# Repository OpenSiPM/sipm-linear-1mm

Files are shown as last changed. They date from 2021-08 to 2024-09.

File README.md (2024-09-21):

# overview
This repository contains a 16 channel linear array detector designed for hyperspectral fluorescense imaging. Each channel is composed of a single 1x1 mm Hamamatsu S14160 SiPM mounted in a carrier board. These feed into 16 pole zero filters and 16 transimpedance amplifiers adapted from the OpenSiPM single channel design.

# pcb
The PCB is a 4 layer board that can be manufactured inexpensive (few dollars plus shipping) from a number of prototyping services. It could additionally be assembled with at least the passive components on relatively inexpensive, or it can be hand soldered via reflow. Aside from the Hamamatsdu SiPM, the components are stock at Digikey/Mouser.

[Linear array bill of materials](http://htmlpreview.github.io/?https://github.com/OpenSiPM/sipm-linear-1mm/blob/main/sipm-linear-s14160/bom/ibom.html)

# power supply
The linear sipm PCB requires a bipolar power supply capable of powering the 16 OPA847 opamps, which have about 20 mA of quescent current each on top of any output current.  This is supplied by the power-supply-linear-array project, which uses two sets of linear and negative regulators combined with a charge pump to generate the required currents. 

[Power supply bill of materials](http://htmlpreview.github.io/?https://github.com/OpenSiPM/sipm-linear-1mm/blob/main/power-supply-linear-array/kicad/bom/ibom.html)

# bias generator
The bias generator provides the high voltage (~49V) required to bias the SPAD cells in the SiPM. Two versions are provided, a standard one using USB-C and a modified one with a second USB-C connector that allows connecting to an external USB-C power supply.  This can be useful as the total array power is about 3W, and so exceeds the 2.5W supplied by USB2 devices.  By using the second port, the power per port can be kept under 500 mA for hubs and hosts that are not USB3 or USB-C.  

[Power supply bill of materials](http://htmlpreview.github.io/?https://github.com/OpenSiPM/sipm-linear-1mm/blob/main/bias-control-lt8364-linear/bom/ibom.html)

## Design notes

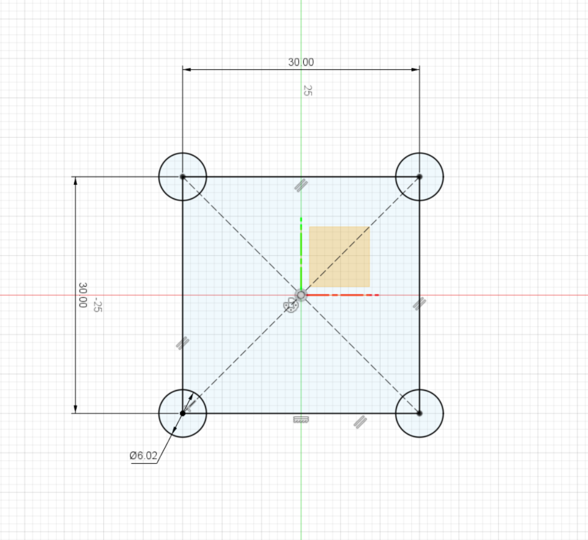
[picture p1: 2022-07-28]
mechanical diagram.png

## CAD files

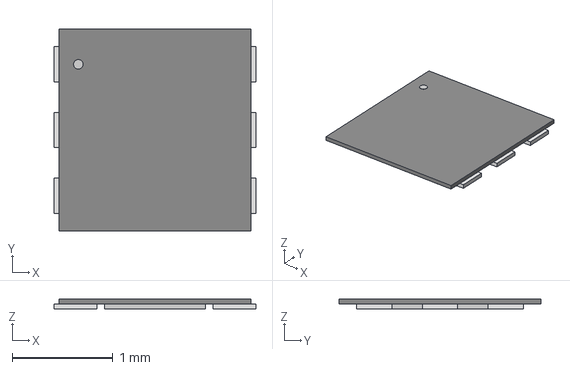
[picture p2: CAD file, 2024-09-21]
bias-control-lt8364-linear-two-usb/step/CP_6_3.step
2.00 x 2.00 x 0.103 mm

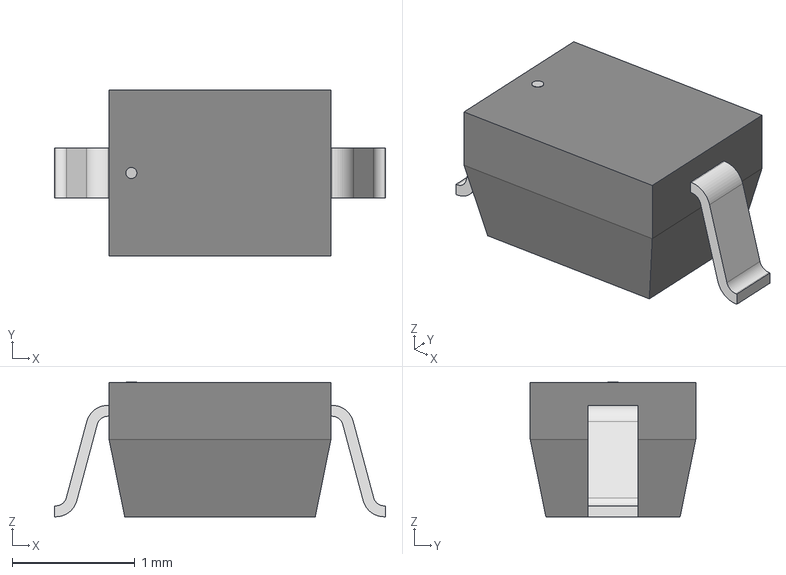
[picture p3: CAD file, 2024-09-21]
bias-control-lt8364-linear/step/SOD323F_NXP.step
2.69 x 1.35 x 1.09 mm

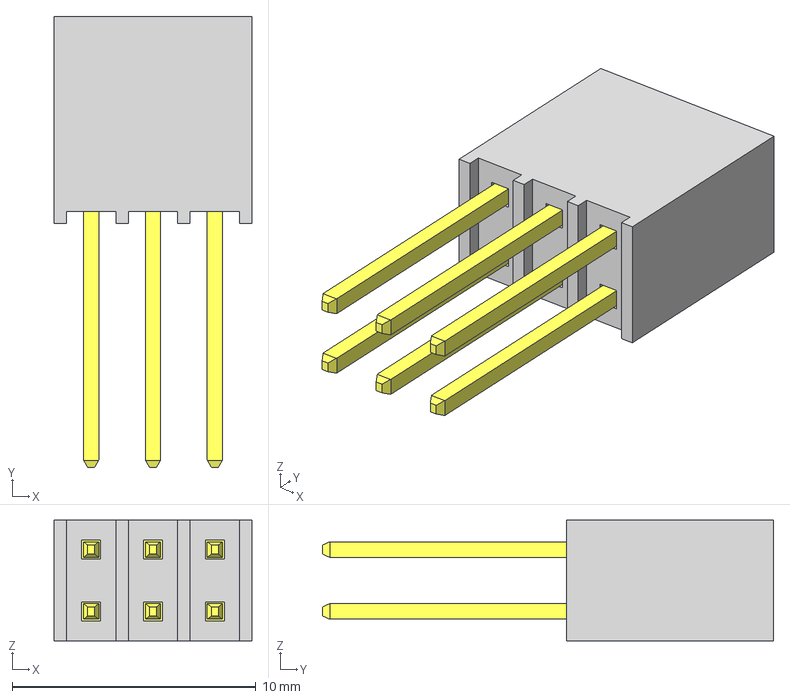
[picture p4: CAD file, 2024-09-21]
power-supply-linear-array/kicad/step/SSQ-103-03-G-D.step
8.13 x 18.5 x 4.95 mm
_T1SSQ-103-03-G-D
_P2SSQ-103-03-G-D

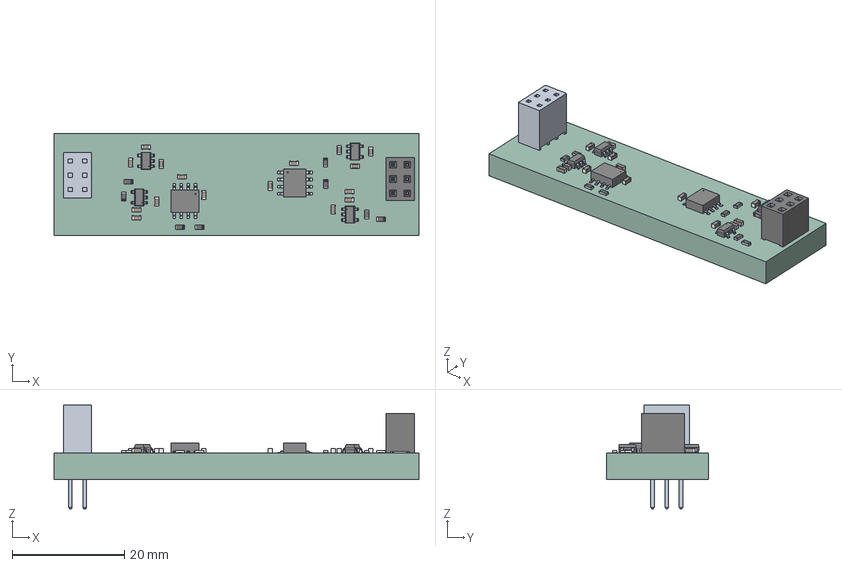
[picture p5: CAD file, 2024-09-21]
power-supply-linear-array/manufacturing/psu.step
65.0 x 18.1 x 18.5 mm
psu PCB

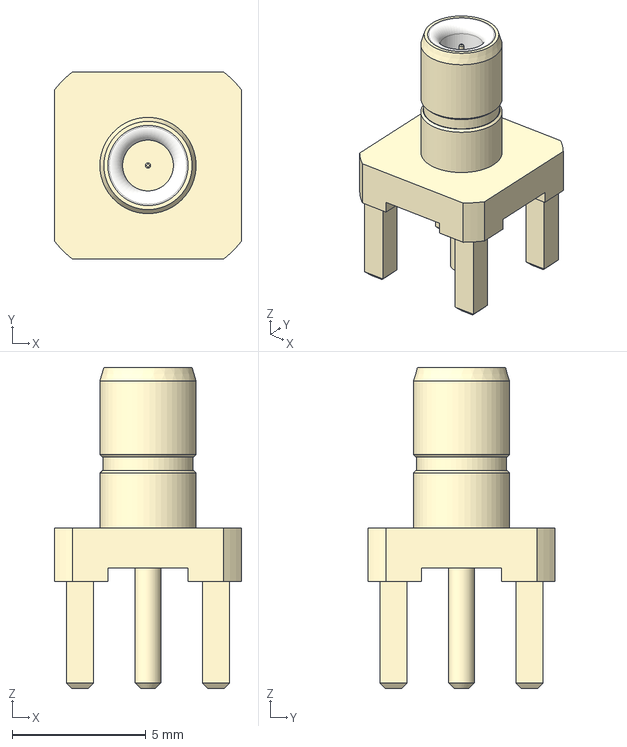
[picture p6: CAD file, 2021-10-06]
sipm-linear-s14160/step/SMB standing.step
7.00 x 7.00 x 12.0 mm

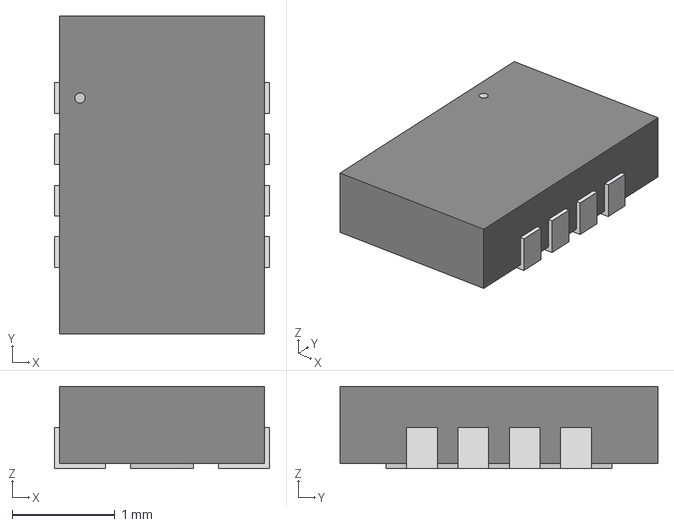
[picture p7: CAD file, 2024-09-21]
bias-control-lt8364-linear-two-usb/step/DFN-8_DDB_LIT-M.step
2.10 x 3.10 x 0.803 mm

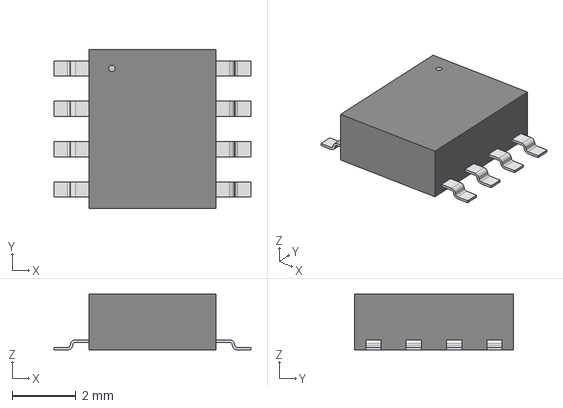
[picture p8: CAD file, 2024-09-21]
power-supply-linear-array/kicad/step/21-0041B_8_MXM.step
6.20 x 5.00 x 1.75 mm

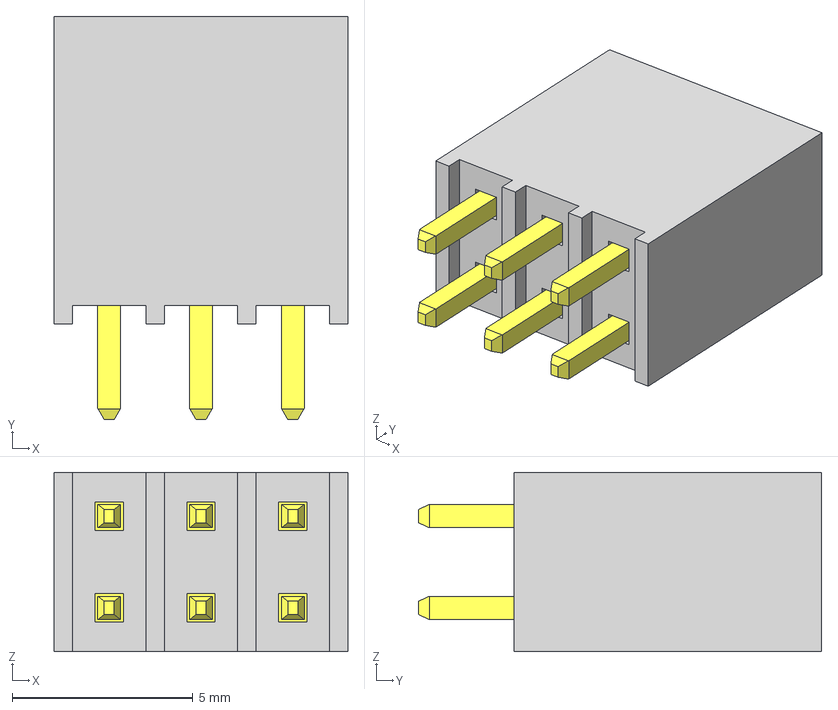
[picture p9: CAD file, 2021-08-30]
sipm-linear-s14160/step/SSQ-103-01-G-D.step
8.13 x 11.2 x 4.95 mm
_T1SSQ-103-01-G-D
_P2SSQ-103-01-G-D

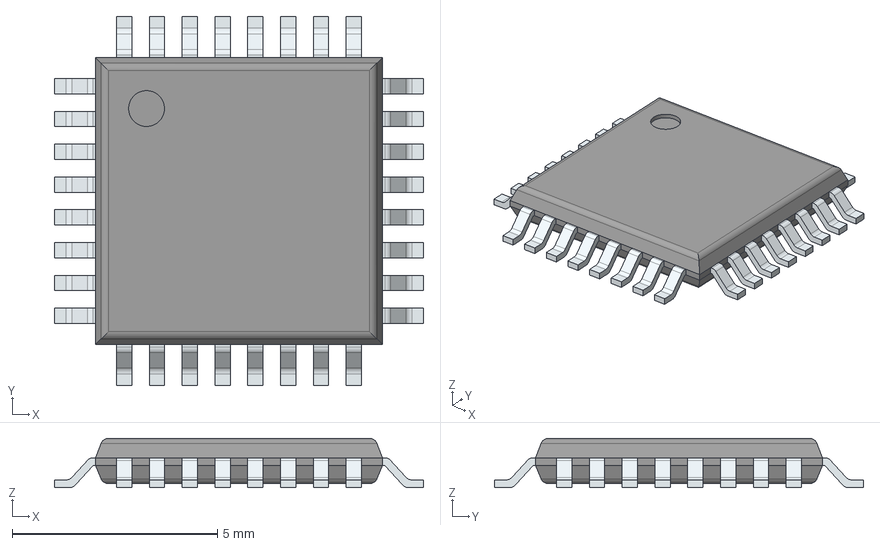
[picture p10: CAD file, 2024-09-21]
bias-control-lt8364-linear-two-usb/step/ATSAMD21E18A-AFT.stp
9.00 x 9.00 x 1.20 mm
PinsArrayLR
PinsArrayTB

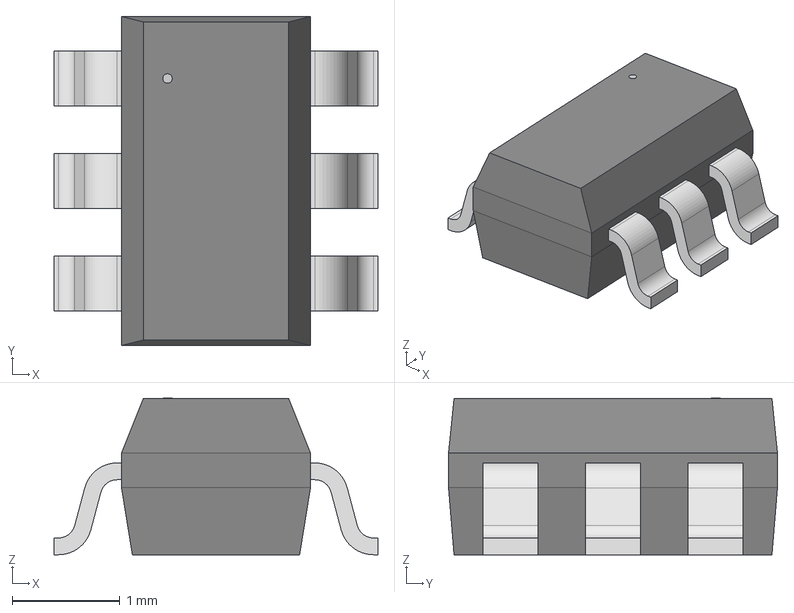
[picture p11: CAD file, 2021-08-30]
power-supply-linear-array/kicad/step/DBV6.step
3.00 x 3.05 x 1.45 mm

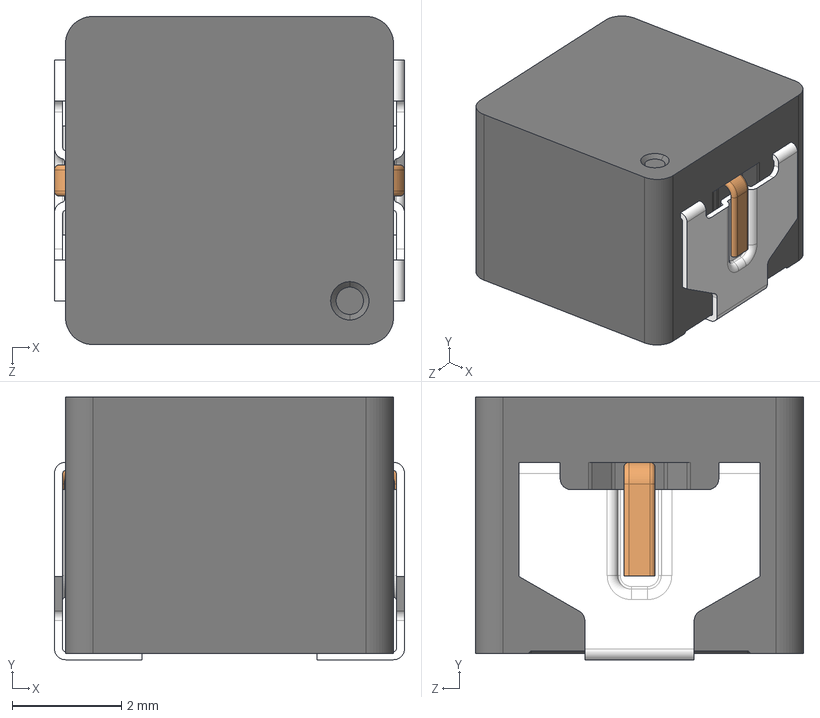
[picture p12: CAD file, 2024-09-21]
bias-control-lt8364-linear/step/ETQP4M3R3KFN.step
6.40 x 4.80 x 6.00 mm

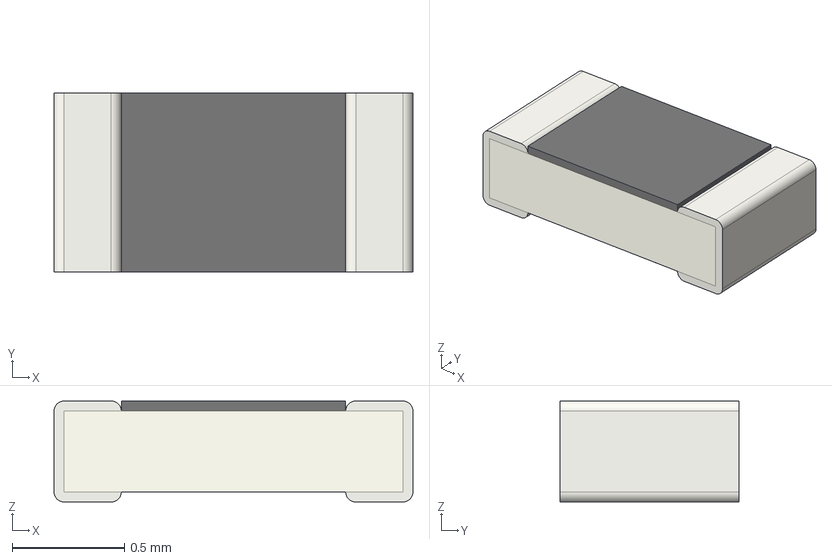
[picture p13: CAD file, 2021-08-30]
power-supply-linear-array/kicad/step/R_0603_1608Metric.step
1.60 x 0.8 x 0.45 mm

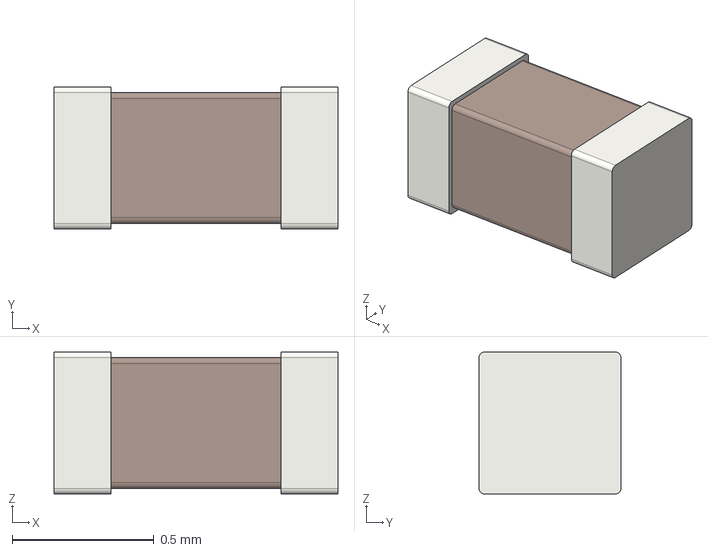
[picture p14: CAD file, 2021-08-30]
sipm-linear-s14160/step/C_0402_1005Metric.step
1.00 x 0.5 x 0.5 mm

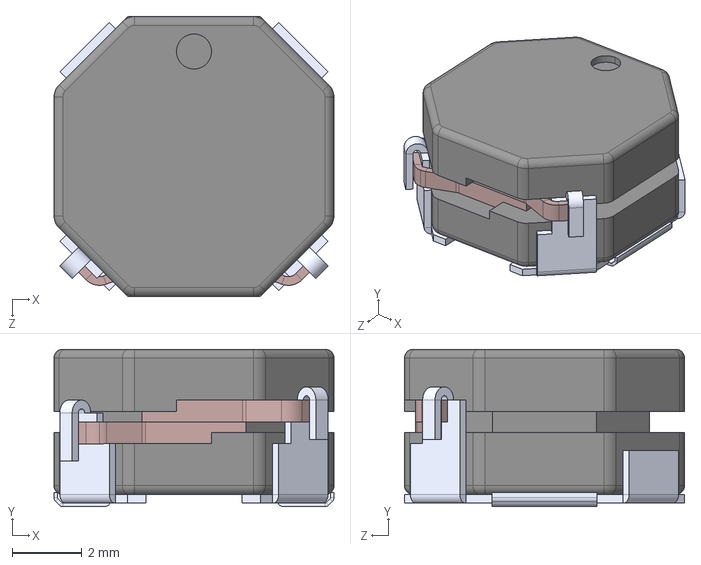
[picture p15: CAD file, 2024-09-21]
bias-control-lt8364-linear-two-usb/step/1217AS-H-3R3N_P3.step
8.00 x 4.50 x 8.00 mm

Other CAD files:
bias-control-lt8364-linear/step/CP_6_3-M.step
bias-control-lt8364-linear-two-usb/step/CP_6_3-L.step
bias-control-lt8364-linear/step/LT3571EUD#PBF.stp
bias-control-lt8364-linear-two-usb/step/878980466.stp
bias-control-lt8364-linear-two-usb/step/CP_6_3-M.step
bias-control-lt8364-linear-two-usb/step/CX80B1-24P_3D_STEP.STEP
bias-control-lt8364-linear-two-usb/step/C_0603_1608Metric.step
bias-control-lt8364-linear-two-usb/step/DFN-8_DDB_LIT-L.step
bias-control-lt8364-linear-two-usb/step/DFN-8_DDB_LIT.step
bias-control-lt8364-linear-two-usb/step/DFN6_2x2MC.step
bias-control-lt8364-linear-two-usb/step/DX07S024WJ3R400--3DModel-STEP-56544.STEP
bias-control-lt8364-linear-two-usb/step/HTSW-103-23-L-D.stp
bias-control-lt8364-linear-two-usb/step/IND_TAIYO_NR6028_TAY.step
bias-control-lt8364-linear-two-usb/step/LT3571EUD#PBF.stp
bias-control-lt8364-linear-two-usb/step/LT8364EMSE#TRPBF.stp
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

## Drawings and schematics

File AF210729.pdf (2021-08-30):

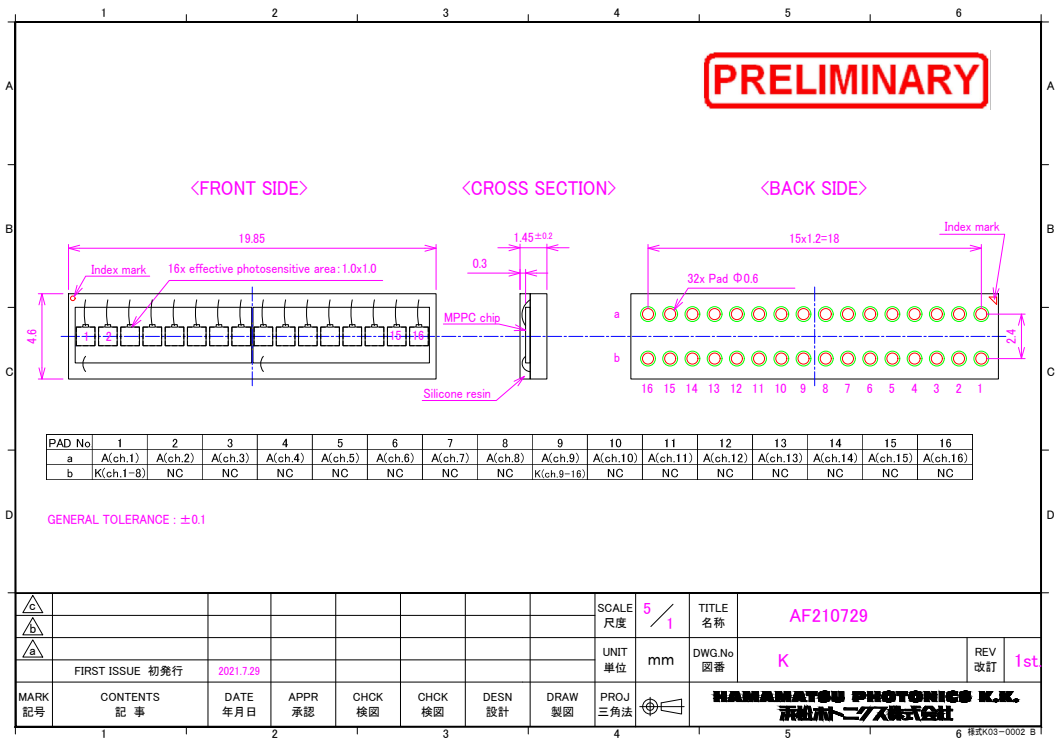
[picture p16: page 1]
15 16 16x effective photosensitive area：1.0x1.0 19.85

2.4 A 6 B 4 5 D 6 様式Ｋ０３－０００２　Ｂ K5 ｍｍ 4 AF210729 C 1 2 3 AB 3 2021.7.29 2 c D ba FIRST ISSUE 初発行 1 C 5 1 MARK 記号 CONTENTS 記 事 DATE 年月日 APPR 承認 CHCK 検図 CHCK 検図 DESN 設計 DRAW 製図 尺度UNIT PROJ 三角法 単位 SCALE 名称 DWG.No 図番 TITLE REV 改訂 1st.

4.6 Index mark 1.45±0.2 0.3 MPPC chip Silicone resin Index mark 32x Pad Φ0.6 <FRONT SIDE> <CROSS SECTION> <BACK SIDE> GENERAL TOLERANCE : ±0.1 16 15 14 13 12 11 10 9 8 7 6 5 4 3 2 1 ba 15x1.2=18

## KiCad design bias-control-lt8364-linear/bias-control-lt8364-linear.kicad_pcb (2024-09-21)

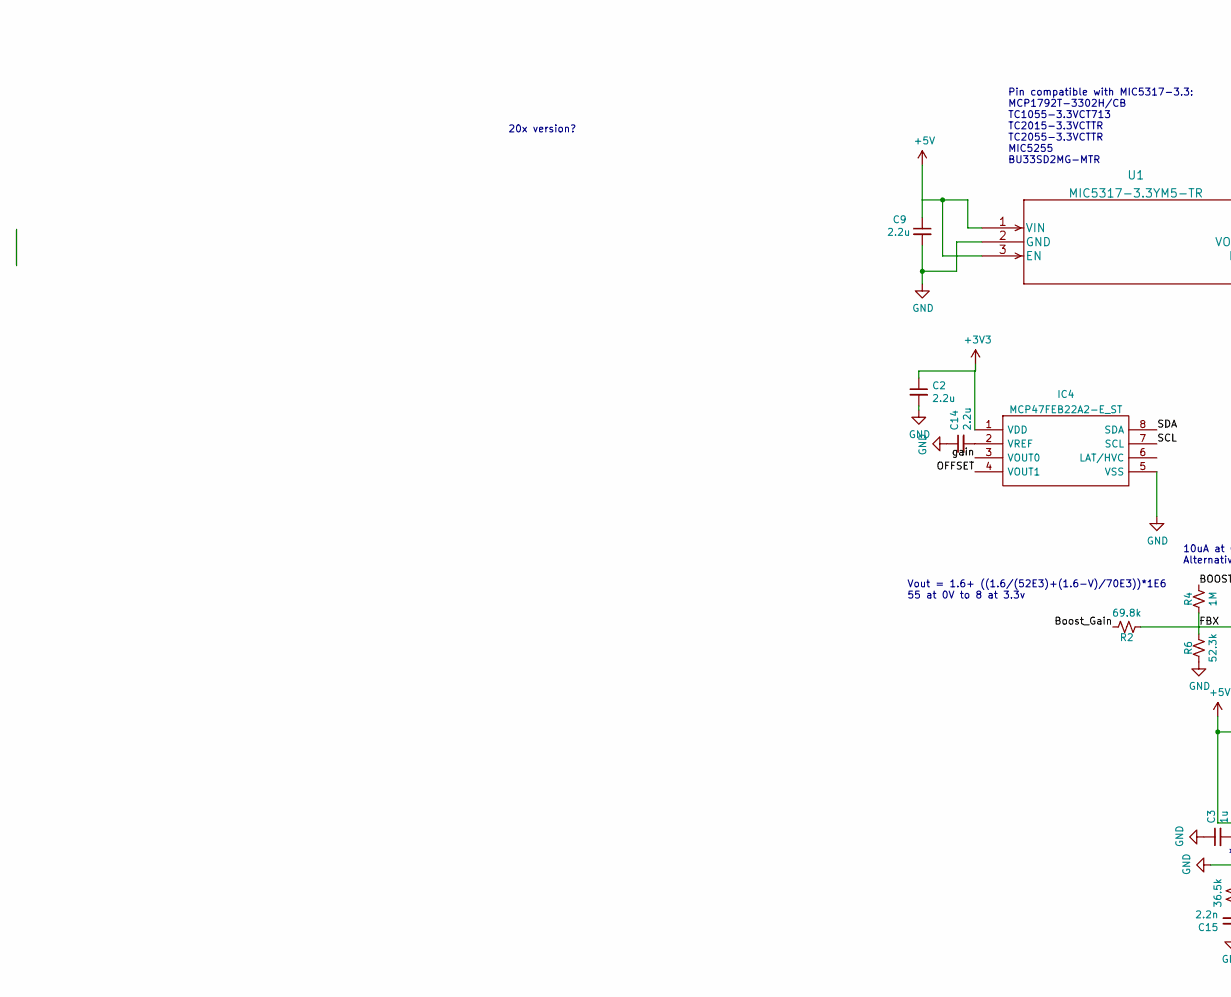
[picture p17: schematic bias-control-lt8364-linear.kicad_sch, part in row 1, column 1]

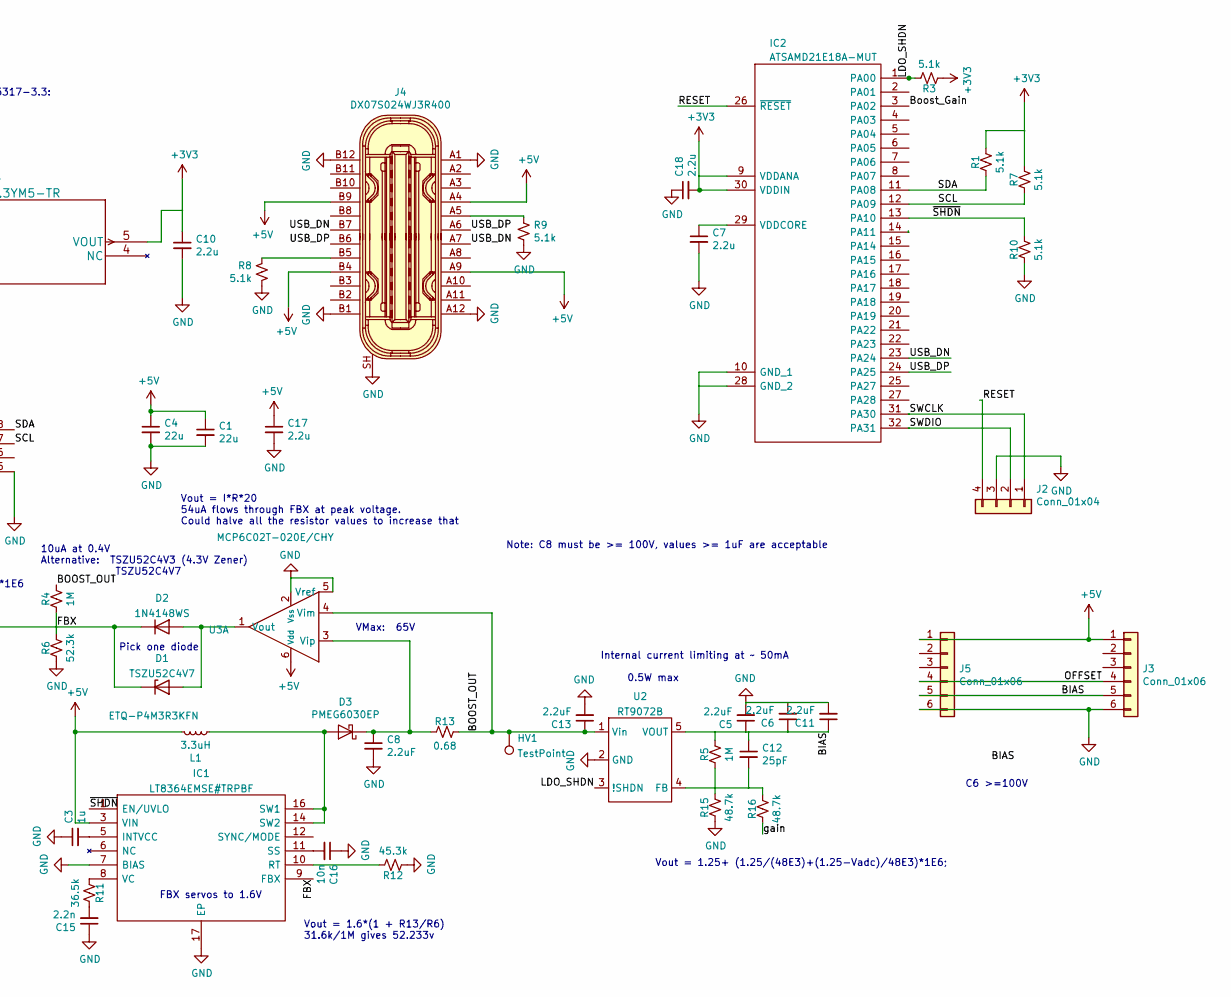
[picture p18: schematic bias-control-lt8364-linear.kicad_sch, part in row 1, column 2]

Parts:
C1, C4: 22u; C_0603_1608Metric; Voltage 10V
C2, C7, C9, C10, C14, C17, C18: 2.2u; C_0402_1005Metric
C3: 1u; C_0402_1005Metric
C5, C6, C8, C11, C13: 2.2uF; C_1206_3216Metric; Voltage 100V
C12: 25pF; C_0402_1005Metric
C15: 2.2n; C_0402_1005Metric
C16: 10n; C_0402_1005Metric
D1: TSZU52C4V7; D_0603_1608Metric
D2: 1N4148WS; D_SOD-323F
D3: PMEG6030EP; D_SOD-128
HV1: TestPoint; TestPoint_Pad_D1.0mm
IC1: LT8364EMSE#TRPBF; LT8364IMSE-PBF; Mouser Part Number 584-LT8364EMSETRPBF
IC2: ATSAMD21E18A-MUT; QFN-32-1EP_5x5mm_Pitch0.5mm; Manufacturer_Part_Number ATSAMD21E18A-AFT
IC4: MCP47FEB22A2-E_ST; SOP65P640X120-8N; Mouser Part Number 579-MCP47FEB22A2EST
J2: Conn_01x04; PinHeader_1x04_P2.54mm_Vertical_SMD_Pin1Right
J3, J5: Conn_01x06; PinHeader_2x03_P2.54mm_Vertical
J4: DX07S024WJ3R400; USB-C_Female_Vert_DX07S024WJ3R400; MPN DX07S024WJ3R400; Digi-Key_PN 670-2950-1-ND
L1: 3.3uH; IND_ETQP4M3R3KFN; MPN ETQ-P4M3R3KFN
R1, R3, R7, R8, R9, R10: 5.1k; R_0402_1005Metric
R2: 69.8k; R_0402_1005Metric
R4, R5: 1M; R_0402_1005Metric
R6: 52.3k; R_0402_1005Metric
R11: 36.5k; R_0402_1005Metric
R12: 45.3k; R_0402_1005Metric
R13: 0.68; R_0402_1005Metric
R15, R16: 48.7k; R_0402_1005Metric
U1: MIC5317-3.3YM5-TR
U2: RT9072B; SOT-23-5
U3: MCP6C02T-020E/CHY; SOT-23-6

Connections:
+3V3: C2.1, C10.1, C18.2, IC2.9 (VDDANA), IC2.30 (VDDIN), IC4.1 (VDD), R1.1, R3.2, R7.1, U1.5 (VOUT)
+5V: C1.1, C4.1, C9.1, C17.1, IC1.3 (VIN), J3.1, J4.A4, J4.A9, J4.B4, J4.B9, J5.1, L1.2, U1.1 (VIN), U1.3 (EN), U3.6 (Vdd)
/BIAS: C5.1, C6.1, C11.1, C12.1, J3.5, J5.5, R5.1, U2.5 (VOUT)
/BOOST_OUT: C13.1, HV1.1, R4.1, R13.1, U2.1 (Vin), U3.4 (Vim)
/Boost_Gain: IC2.3 (PA02), R2.1
/FBX: D1.1 (K), D2.1 (K), IC1.9 (FBX), R2.2, R4.2, R6.1
/LDO_SHDN: IC2.1 (PA00), R3.1, U2.3 (!SHDN)
/OFFSET: IC4.4 (VOUT1), J3.4, J5.4
/RESET: IC2.26 (~RESET), J2.4
/SCL: IC2.12 (PA09), IC4.7 (SCL), R7.2
/SDA: IC2.11 (PA08), IC4.8 (SDA), R1.2
/SWCLK: IC2.31 (PA30), J2.1
/SWDIO: IC2.32 (PA31), J2.2
/USB_DN: IC2.23 (PA24), J4.A7, J4.B7
/USB_DP: IC2.24 (PA25), J4.A6, J4.B6
/gain: IC4.3 (VOUT0), R16.2
/~SHDN: IC1.1 (EN/UVLO), IC2.13 (PA10), R10.1
GND: C1.2, C2.2, C3.1, C4.2, C5.2, C6.2, C7.2, C8.2, C9.2, C10.2, C11.2, C13.2, C14.1, C15.1, C16.1, C17.2, C18.1, IC1.7 (BIAS), IC1.17 (EP), IC2.10 (GND_1), IC2.28 (GND_2), IC2.33 (EP), IC4.5 (VSS), J2.3, J3.6, J4.A1, J4.A12, J4.B1, J4.B12, J4.SH, J5.6, R6.2, R8.2, R9.2, R10.2, R12.2, R15.2, U1.2 (GND), U2.2 (GND), U3.2 (Vss), U3.5 (Vref)
unnamed: C15.2, R11.1
unnamed: D1.2 (A), D2.2 (A), U3.1 (Vout)
unnamed: D3.2 (A), IC1.14 (SW2), IC1.16 (SW1), L1.1
unnamed: C8.1, D3.1 (K), R13.2, U3.3 (Vip)
unnamed: C3.2, IC1.5 (INTVCC)
unnamed: IC1.10 (RT), R12.1
unnamed: C16.2, IC1.11 (SS)
unnamed: IC1.8 (VC), R11.2
unnamed: C7.1, IC2.29 (VDDCORE)
unnamed: C14.2, IC4.2 (VREF)
unnamed: J4.A5, R9.1
unnamed: J4.B5, R8.1
unnamed: C12.2, R5.2, R15.1, R16.1, U2.4 (FB)

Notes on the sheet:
Vout = 1.6*(1 + R13/R6) 31.6k/1M gives 52.233v
Note: C8 must be >= 100V, values >= 1uF are acceptable
Vout = I*R*20 54uA flows through FBX at peak voltage. Could halve all the resistor values to increase that
Pick one diode
Internal current limiting at ~ 50mA
Pin compatible with MIC5317-3.3: MCP1792T-3302H/CB TC1055-3.3VCT713 TC2015-3.3VCTTR TC2055-3.3VCTTR MIC5255 BU33SD2MG-MTR
20x version?
0.5W max
10uA at 0.4V Alternative: TSZU52C4V3 (4.3V Zener) TSZU52C4V7
C6 >=100V
Vout = 1.25+ (1.25/(48E3)+(1.25-Vadc)/48E3)*1E6;
VMax: 65V
Vout = 1.6+ ((1.6/(52E3)+(1.6-V)/70E3))*1E6 55 at 0V to 8 at 3.3v
FBX servos to 1.6V

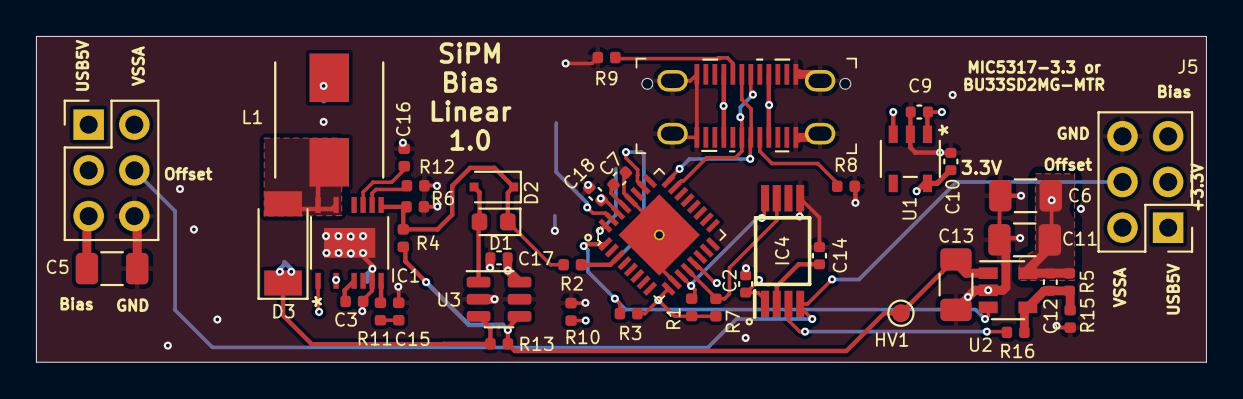
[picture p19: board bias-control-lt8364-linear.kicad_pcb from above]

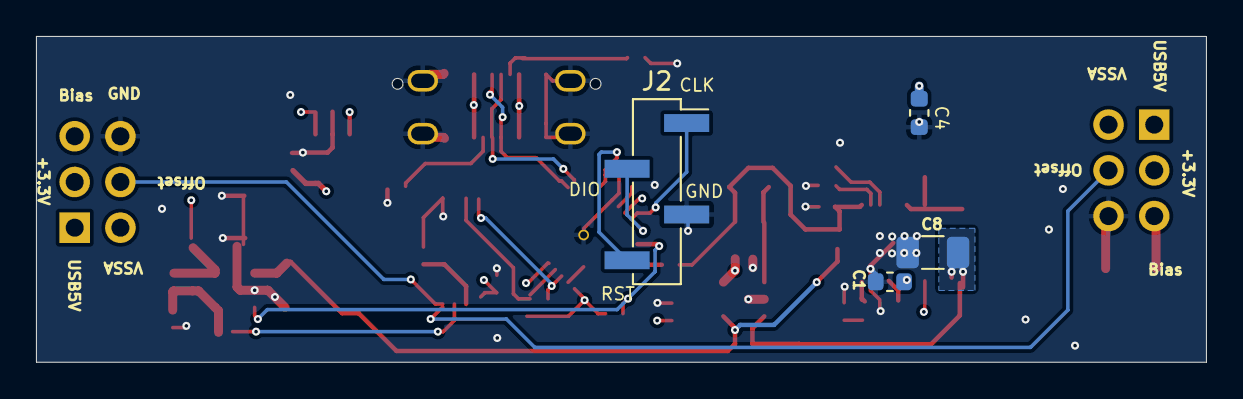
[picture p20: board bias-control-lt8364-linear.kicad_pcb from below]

Board: 4 copper layers, 65.0 x 18.1 mm, 48 parts (4 on the bottom side), 31 nets.

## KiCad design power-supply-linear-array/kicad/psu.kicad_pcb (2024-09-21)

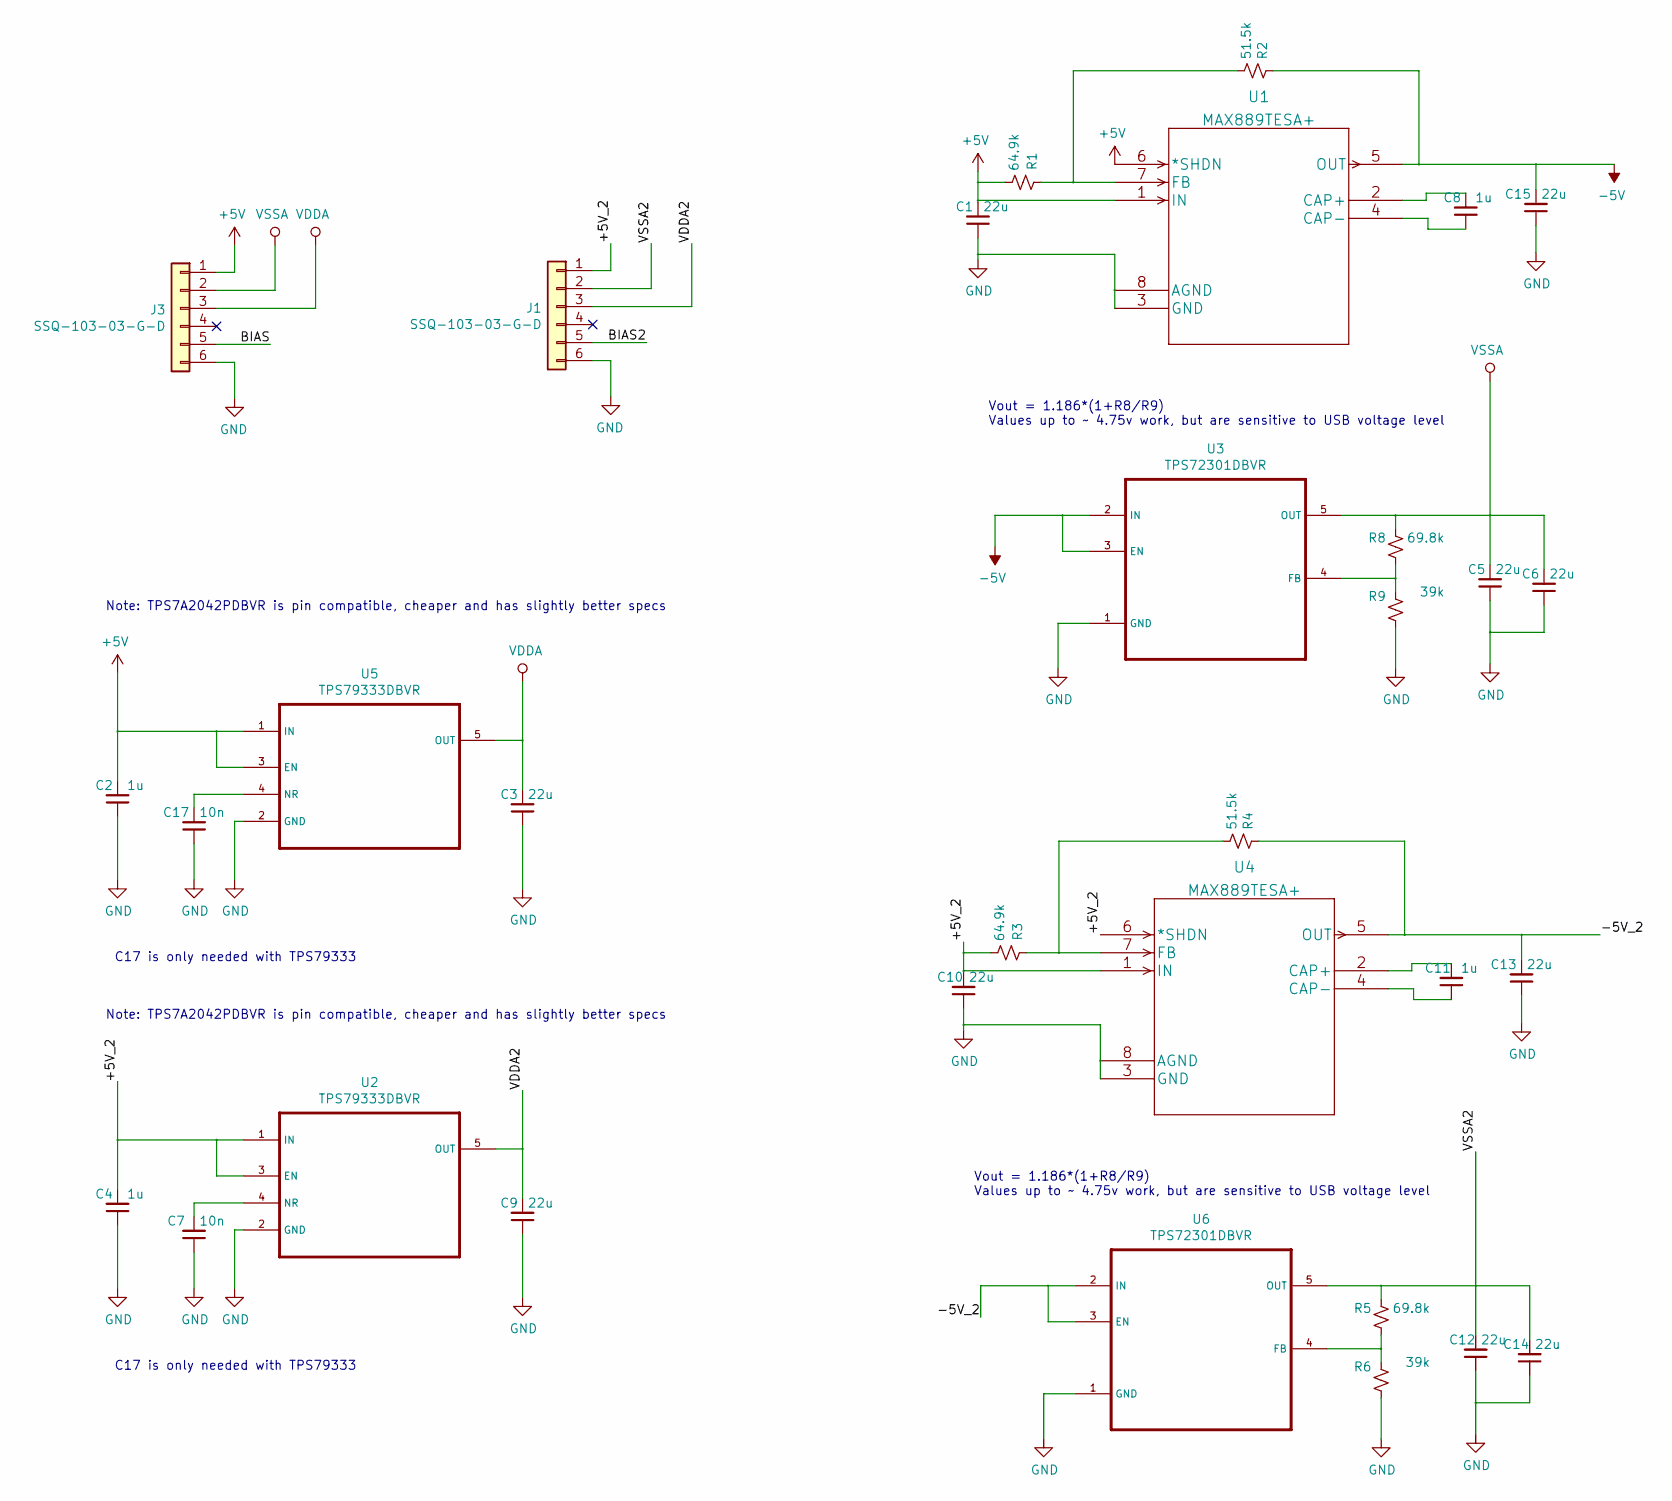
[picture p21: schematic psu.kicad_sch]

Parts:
C1, C3, C5, C6, C9, C10, C12, C13, C14, C15: 22u; C_0603_1608Metric
C2, C4, C8, C11: 1u; C_0603_1608Metric
C7, C17: 10n; C_0603_1608Metric
J1, J3: SSQ-103-03-G-D; PinHeader_2x03_P2.54mm_Vertical
R1, R3: 64.9k; R_0603_1608Metric
R2, R4: 51.5k; R_0603_1608Metric
R5, R8: 69.8k; R_0603_1608Metric
R6, R9: 39k; R_0603_1608Metric
U1, U4: MAX889TESA+; MAX889TESA&plus_
U2, U5: TPS79333DBVR
U3, U6: TPS72301DBVR

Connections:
+5V: C1.2, C2.2, J3.1, R1.2, U1.1 (IN), U1.6 (*SHDN), U5.1 (IN), U5.3 (EN)
-5V: C15.2, R2.1, U1.5 (OUT), U3.2 (IN), U3.3 (EN)
/+5V_2: C4.2, C10.2, J1.1, R3.2, U2.1 (IN), U2.3 (EN), U4.1 (IN), U4.6 (*SHDN)
/-5V_2: C13.2, R4.1, U4.5 (OUT), U6.2 (IN), U6.3 (EN)
/BIAS: J3.5
/BIAS2: J1.5
/VDDA2: C9.2, J1.3, U2.5 (OUT)
/VSSA2: C12.2, C14.2, J1.2, R5.2, U6.5 (OUT)
GND: C1.1, C2.1, C3.1, C4.1, C5.1, C6.1, C7.1, C9.1, C10.1, C12.1, C13.1, C14.1, C15.1, C17.1, J1.6, J3.6, R6.1, R9.1, U1.3 (GND), U1.8 (AGND), U2.2 (GND), U3.1 (GND), U4.3 (GND), U4.8 (AGND), U5.2 (GND), U6.1 (GND)
unnamed: C8.2, U1.2 (CAP+)
unnamed: C8.1, U1.4 (CAP-)
unnamed: R1.1, R2.2, U1.7 (FB)
unnamed: C7.2, U2.4 (NR)
unnamed: R8.1, R9.2, U3.4 (FB)
unnamed: C11.2, U4.2 (CAP+)
unnamed: C11.1, U4.4 (CAP-)
unnamed: R3.1, R4.2, U4.7 (FB)
unnamed: C17.2, U5.4 (NR)
unnamed: R5.1, R6.2, U6.4 (FB)
VDDA: C3.2, J3.3, U5.5 (OUT)
VSSA: C5.2, C6.2, J3.2, R8.2, U3.5 (OUT)

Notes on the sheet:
Vout = 1.186*(1+R8/R9) Values up to ~ 4.75v work, but are sensitive to USB voltage level
Note: TPS7A2042PDBVR is pin compatible, cheaper and has slightly better specs
C17 is only needed with TPS79333

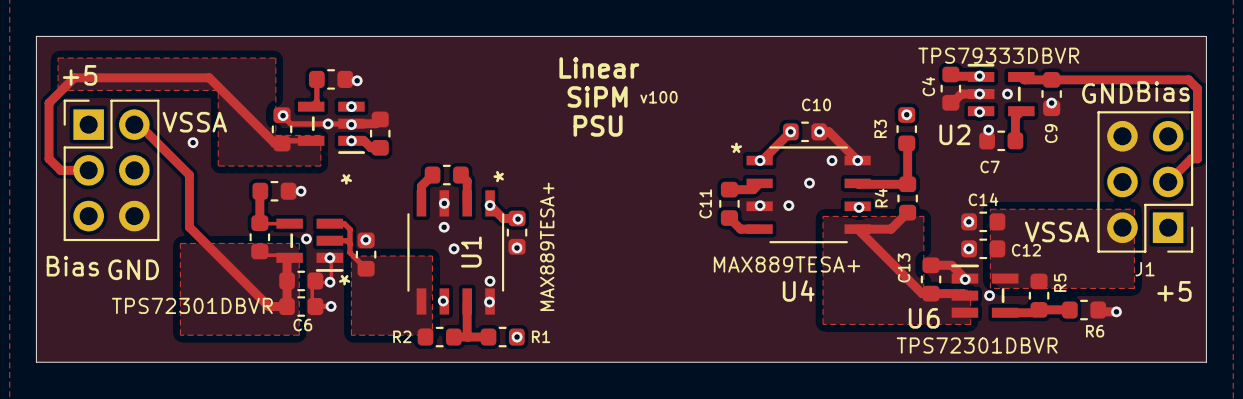
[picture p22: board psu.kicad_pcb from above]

Board: 4 copper layers, 65.0 x 18.1 mm, 32 parts (0 on the bottom side), 19 nets.

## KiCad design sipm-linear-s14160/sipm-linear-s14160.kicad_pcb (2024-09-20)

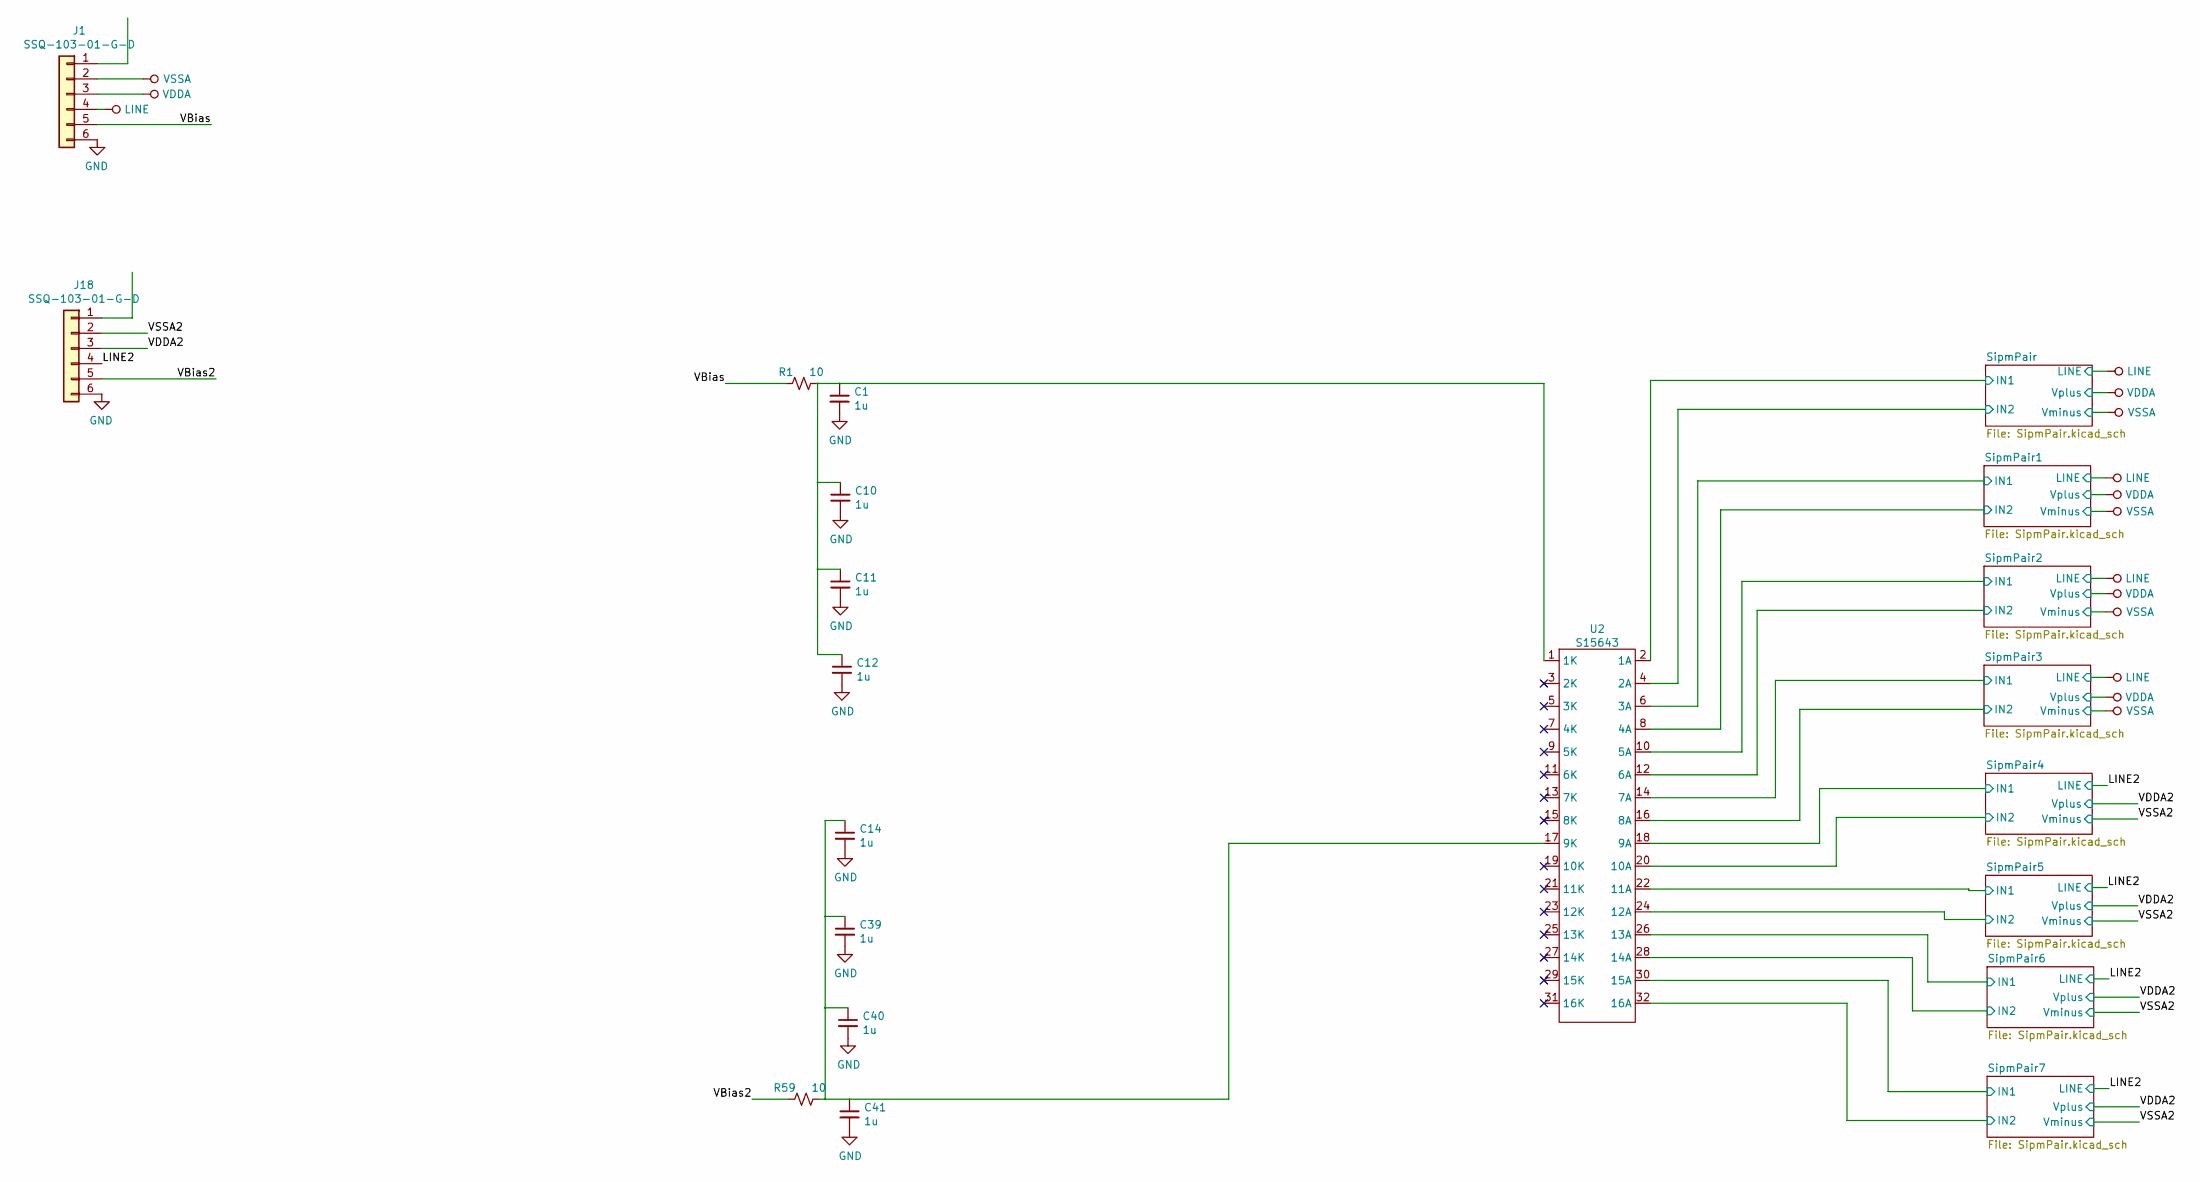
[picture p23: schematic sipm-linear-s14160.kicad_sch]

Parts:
C1, C10, C11, C12, C14, C39, C40, C41: 1u; C_1206_3216Metric; Voltage 100V
J1, J18: SSQ-103-01-G-D; PinHeader_2x03_P2.54mm_Vertical
R1, R59: 10; R_0402_1005Metric
U2: S15643; AF210729-S14160-x16

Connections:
/LINE2: J18.4; also elsewhere on the board
/SipmPair1/IN1: U2.6 (3A); also elsewhere on the board
/SipmPair1/IN2: U2.8 (4A); also elsewhere on the board
/SipmPair2/IN1: U2.10 (5A); also elsewhere on the board
/SipmPair2/IN2: U2.12 (6A); also elsewhere on the board
/SipmPair3/IN1: U2.14 (7A); also elsewhere on the board
/SipmPair3/IN2: U2.16 (8A); also elsewhere on the board
/SipmPair4/IN1: U2.18 (9A); also elsewhere on the board
/SipmPair4/IN2: U2.20 (10A); also elsewhere on the board
/SipmPair5/IN1: U2.22 (11A); also elsewhere on the board
/SipmPair5/IN2: U2.24 (12A); also elsewhere on the board
/SipmPair6/IN1: U2.26 (13A); also elsewhere on the board
/SipmPair6/IN2: U2.28 (14A); also elsewhere on the board
/SipmPair7/IN1: U2.30 (15A); also elsewhere on the board
/SipmPair7/IN2: U2.32 (16A); also elsewhere on the board
/SipmPair/IN1: U2.2 (1A); also elsewhere on the board
/SipmPair/IN2: U2.4 (2A); also elsewhere on the board
/VBias: J1.5, R1.1
/VBias2: J18.5, R59.1
/VDDA2: J18.3; also elsewhere on the board
/VSSA2: J18.2; also elsewhere on the board
GND: C1.2, C10.2, C11.2, C12.2, C14.2, C39.2, C40.2, C41.2, J1.6, J18.6; also elsewhere on the board
LINE: J1.4; also elsewhere on the board
unnamed: C1.1, C10.1, C11.1, C12.1, R1.2, U2.1 (1K)
unnamed: C14.1, C39.1, C40.1, C41.1, R59.2, U2.17 (9K)
VDDA: J1.3; also elsewhere on the board
VSSA: J1.2; also elsewhere on the board

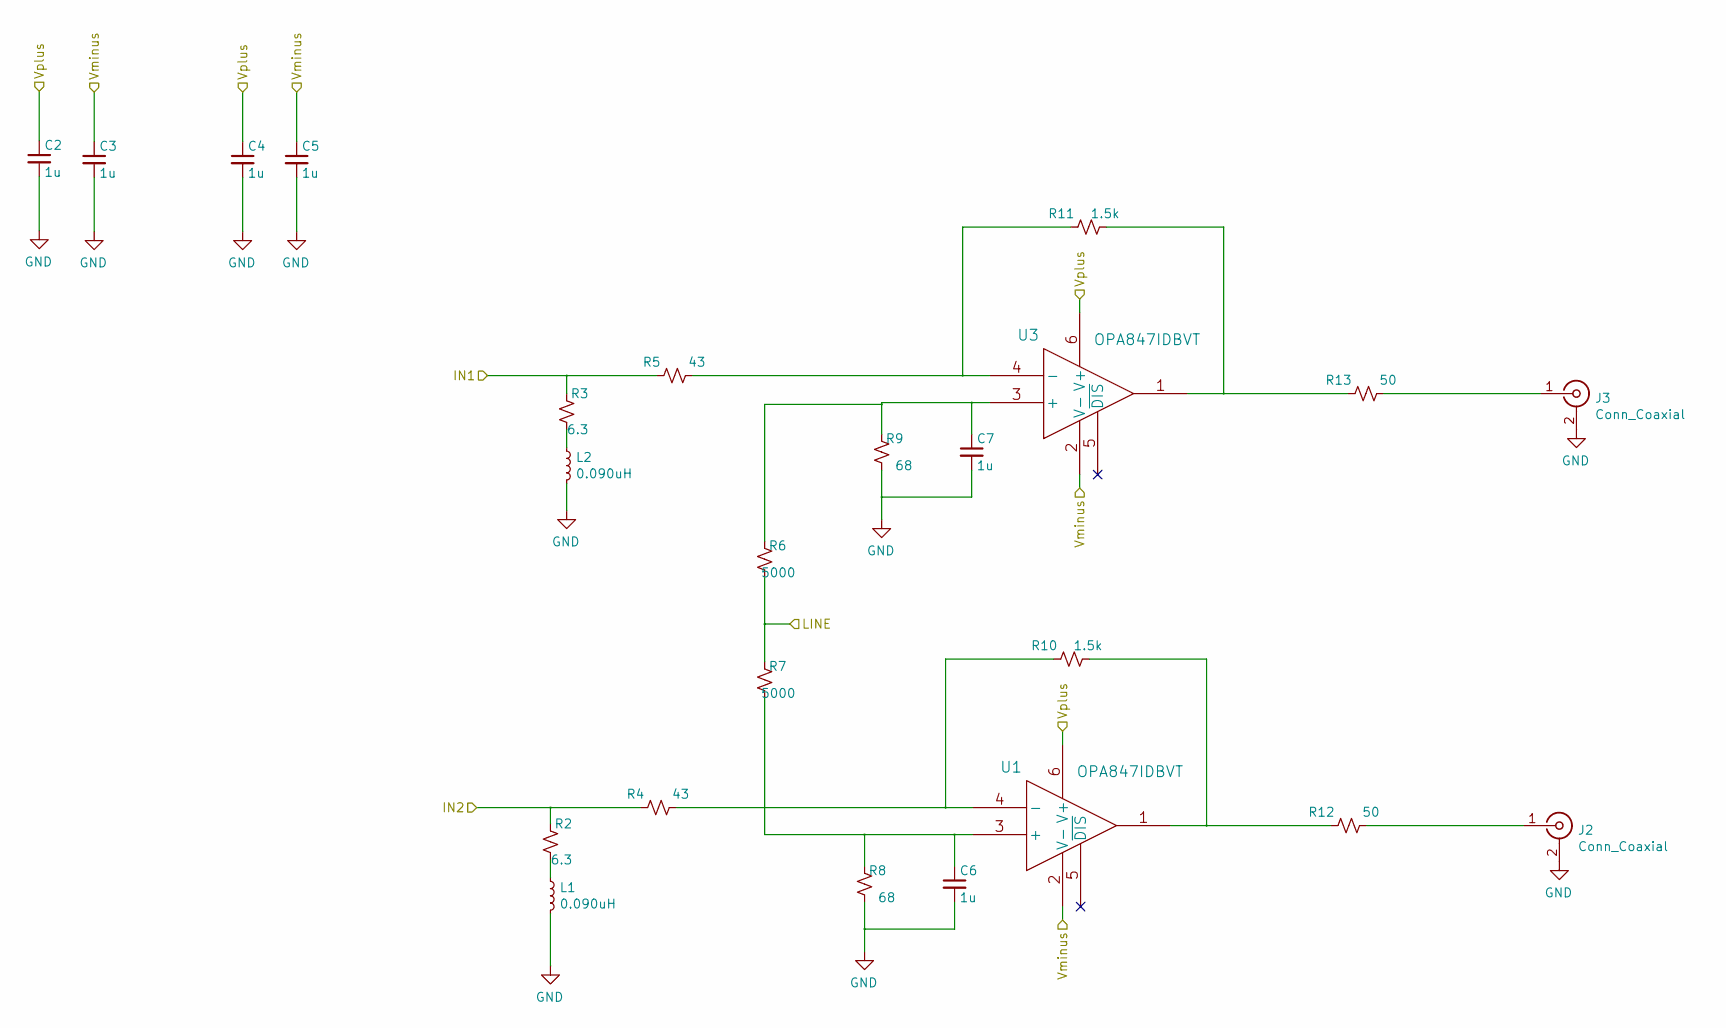
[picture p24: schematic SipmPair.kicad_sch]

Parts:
C2, C3, C4, C5, C6, C7: 1u; C_0402_1005Metric; Voltage 16V
J2, J3: Conn_Coaxial; SMB_Jack_Vertical; Digikey WM5528-ND
L1, L2: 0.090uH; C_0402_1005Metric
R2, R3: 6.3; R_0402_1005Metric
R4, R5: 43; R_0402_1005Metric
R6, R7: 5000; R_0402_1005Metric
R8, R9: 68; R_0402_1005Metric
R10, R11: 1.5k; R_0402_1005Metric
R12, R13: 50; R_0402_1005Metric
U1, U3: OPA847IDBVT

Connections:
/SipmPair1/IN1: R3.2, R5.1; also elsewhere on the board
/SipmPair1/IN2: R2.2, R4.1; also elsewhere on the board
GND: C2.2, C3.2, C4.2, C5.2, C6.2, C7.2, J2.2 (Ext), J3.2 (Ext), L1.2, L2.2, R8.1, R9.1; also elsewhere on the board
LINE: R6.1, R7.2; also elsewhere on the board
unnamed: J2.1 (In), R12.2
unnamed: J3.1 (In), R13.2
unnamed: L1.1, R2.1
unnamed: L2.1, R3.1
unnamed: R10.2, R12.1, U1.1
unnamed: R11.2, R13.1, U3.1
unnamed: C6.1, R7.1, R8.2, U1.3 (+)
unnamed: R4.2, R10.1, U1.4 (-)
unnamed: C7.1, R6.2, R9.2, U3.3 (+)
unnamed: R5.2, R11.1, U3.4 (-)
VDDA: C2.1, C4.1, U1.6 (V+), U3.6 (V+); also elsewhere on the board
VSSA: C3.1, C5.1, U1.2 (V-), U3.2 (V-); also elsewhere on the board

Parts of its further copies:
C15, C16, C17, C18, C19, C20, C23, C24, C25, C26, C27, C28, C31, C32, C33, C34, C35, C36, C42, C43, C44, C45, C46, C47, C57, C58, C59, C60, C61, C62, C65, C66, C67, C68, C69, C70, C73, C74, C75, C76, C77, C78: 1u; C_0402_1005Metric; Voltage 16V
J4, J5, J6, J7, J8, J9, J10, J11, J12, J13, J14, J15, J16, J17: Conn_Coaxial; SMB_Jack_Vertical; Digikey WM5528-ND
L3, L4, L5, L6, L7, L8, L9, L10, L11, L12, L13, L14, L15, L16: 0.090uH; C_0402_1005Metric
R14, R15, R25, R26, R37, R38, R49, R50, R81, R82, R93, R94, R105, R106: 5000; R_0402_1005Metric
R21, R22, R33, R34, R45, R46, R62, R63, R77, R78, R89, R90, R101, R102: 6.3; R_0402_1005Metric
R23, R24, R35, R36, R47, R48, R64, R65, R79, R80, R91, R92, R103, R104: 43; R_0402_1005Metric
R27, R28, R39, R40, R51, R52, R68, R69, R83, R84, R95, R96, R107, R108: 68; R_0402_1005Metric
R29, R30, R41, R42, R53, R54, R70, R71, R85, R86, R97, R98, R109, R110: 1.5k; R_0402_1005Metric
R31, R32, R43, R44, R55, R56, R72, R73, R87, R88, R99, R100, R111, R112: 50; R_0402_1005Metric
U4, U5, U6, U7, U8, U9, U10, U11, U12, U13, U14, U15, U16, U17: OPA847IDBVT

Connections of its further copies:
/LINE2: R49.1, R50.2, R81.1, R82.2, R93.1, R94.2, R105.1, R106.2; also elsewhere on the board
/SipmPair2/IN1: R22.2, R24.1; also elsewhere on the board
/SipmPair2/IN2: R21.2, R23.1; also elsewhere on the board
/SipmPair3/IN1: R34.2, R36.1; also elsewhere on the board
/SipmPair3/IN2: R33.2, R35.1; also elsewhere on the board
/SipmPair4/IN1: R46.2, R48.1; also elsewhere on the board
/SipmPair4/IN2: R45.2, R47.1; also elsewhere on the board
/SipmPair5/IN1: R78.2, R80.1; also elsewhere on the board
/SipmPair5/IN2: R77.2, R79.1; also elsewhere on the board
/SipmPair6/IN1: R90.2, R92.1; also elsewhere on the board
/SipmPair6/IN2: R89.2, R91.1; also elsewhere on the board
/SipmPair7/IN1: R102.2, R104.1; also elsewhere on the board
/SipmPair7/IN2: R101.2, R103.1; also elsewhere on the board
/SipmPair/IN1: R63.2, R65.1; also elsewhere on the board
/SipmPair/IN2: R62.2, R64.1; also elsewhere on the board
/VDDA2: C31.1, C33.1, C57.1, C59.1, C65.1, C67.1, C73.1, C75.1, U8.6 (V+), U9.6 (V+), U10.6 (V+), U11.6 (V+), U14.6 (V+), U15.6 (V+), U16.6 (V+), U17.6 (V+); also elsewhere on the board
/VSSA2: C32.1, C34.1, C58.1, C60.1, C66.1, C68.1, C74.1, C76.1, U8.2 (V-), U9.2 (V-), U10.2 (V-), U11.2 (V-), U14.2 (V-), U15.2 (V-), U16.2 (V-), U17.2 (V-); also elsewhere on the board
GND: C15.2, C16.2, C17.2, C18.2, C19.2, C20.2, C23.2, C24.2, C25.2, C26.2, C27.2, C28.2, C31.2, C32.2, C33.2, C34.2, C35.2, C36.2, C42.2, C43.2, C44.2, C45.2, C46.2, C47.2, C57.2, C58.2, C59.2, C60.2, C61.2, C62.2, C65.2, C66.2, C67.2, C68.2, C69.2, C70.2, C73.2, C74.2, C75.2, C76.2, C77.2, C78.2, J4.2 (Ext), J5.2 (Ext), J6.2 (Ext), J7.2 (Ext), J8.2 (Ext), J9.2 (Ext), J10.2 (Ext), J11.2 (Ext), J12.2 (Ext), J13.2 (Ext), J14.2 (Ext), J15.2 (Ext), J16.2 (Ext), J17.2 (Ext), L3.2, L4.2, L5.2, L6.2, L7.2, L8.2, L9.2, L10.2, L11.2, L12.2, L13.2, L14.2, L15.2, L16.2, R27.1, R28.1, R39.1, R40.1, R51.1, R52.1, R68.1, R69.1, R83.1, R84.1, R95.1, R96.1, R107.1, R108.1; also elsewhere on the board
LINE: R14.1, R15.2, R25.1, R26.2, R37.1, R38.2; also elsewhere on the board
unnamed: J4.1 (In), R31.2
unnamed: J5.1 (In), R32.2
unnamed: J6.1 (In), R43.2
unnamed: J7.1 (In), R44.2
unnamed: J8.1 (In), R55.2
unnamed: J9.1 (In), R56.2
unnamed: J10.1 (In), R87.2
unnamed: J11.1 (In), R88.2
unnamed: J12.1 (In), R72.2
unnamed: J13.1 (In), R73.2
unnamed: J14.1 (In), R99.2
unnamed: J15.1 (In), R100.2
unnamed: J16.1 (In), R111.2
unnamed: J17.1 (In), R112.2
unnamed: L3.1, R21.1
unnamed: L4.1, R22.1
unnamed: L5.1, R33.1
unnamed: L6.1, R34.1
unnamed: L7.1, R45.1
unnamed: L8.1, R46.1
unnamed: L9.1, R77.1
unnamed: L10.1, R78.1
unnamed: L11.1, R62.1
unnamed: L12.1, R63.1
unnamed: L13.1, R89.1
unnamed: L14.1, R90.1
unnamed: L15.1, R101.1
unnamed: L16.1, R102.1
unnamed: R29.2, R31.1, U4.1
unnamed: R30.2, R32.1, U5.1
unnamed: R41.2, R43.1, U6.1
unnamed: R42.2, R44.1, U7.1
unnamed: R53.2, R55.1, U8.1
unnamed: R54.2, R56.1, U9.1
unnamed: R70.2, R72.1, U12.1
unnamed: R71.2, R73.1, U13.1
unnamed: R85.2, R87.1, U10.1
unnamed: R86.2, R88.1, U11.1
unnamed: R97.2, R99.1, U14.1
unnamed: R98.2, R100.1, U15.1
unnamed: R109.2, R111.1, U16.1
unnamed: R110.2, R112.1, U17.1
unnamed: C19.1, R26.1, R27.2, U4.3 (+)
unnamed: R23.2, R29.1, U4.4 (-)
unnamed: C20.1, R25.2, R28.2, U5.3 (+)
unnamed: R24.2, R30.1, U5.4 (-)
unnamed: C27.1, R38.1, R39.2, U6.3 (+)
unnamed: R35.2, R41.1, U6.4 (-)
unnamed: C28.1, R37.2, R40.2, U7.3 (+)
unnamed: R36.2, R42.1, U7.4 (-)
unnamed: C35.1, R50.1, R51.2, U8.3 (+)
unnamed: R47.2, R53.1, U8.4 (-)
unnamed: C36.1, R49.2, R52.2, U9.3 (+)
unnamed: R48.2, R54.1, U9.4 (-)
unnamed: C61.1, R82.1, R83.2, U10.3 (+)
unnamed: R79.2, R85.1, U10.4 (-)
unnamed: C62.1, R81.2, R84.2, U11.3 (+)
unnamed: R80.2, R86.1, U11.4 (-)
unnamed: C46.1, R15.1, R68.2, U12.3 (+)
unnamed: R64.2, R70.1, U12.4 (-)
unnamed: C47.1, R14.2, R69.2, U13.3 (+)
unnamed: R65.2, R71.1, U13.4 (-)
unnamed: C69.1, R94.1, R95.2, U14.3 (+)
unnamed: R91.2, R97.1, U14.4 (-)
unnamed: C70.1, R93.2, R96.2, U15.3 (+)
unnamed: R92.2, R98.1, U15.4 (-)
unnamed: C77.1, R106.1, R107.2, U16.3 (+)
unnamed: R103.2, R109.1, U16.4 (-)
unnamed: C78.1, R105.2, R108.2, U17.3 (+)
unnamed: R104.2, R110.1, U17.4 (-)
VDDA: C15.1, C17.1, C23.1, C25.1, C42.1, C44.1, U4.6 (V+), U5.6 (V+), U6.6 (V+), U7.6 (V+), U12.6 (V+), U13.6 (V+); also elsewhere on the board
VSSA: C16.1, C18.1, C24.1, C26.1, C43.1, C45.1, U4.2 (V-), U5.2 (V-), U6.2 (V-), U7.2 (V-), U12.2 (V-), U13.2 (V-); also elsewhere on the board

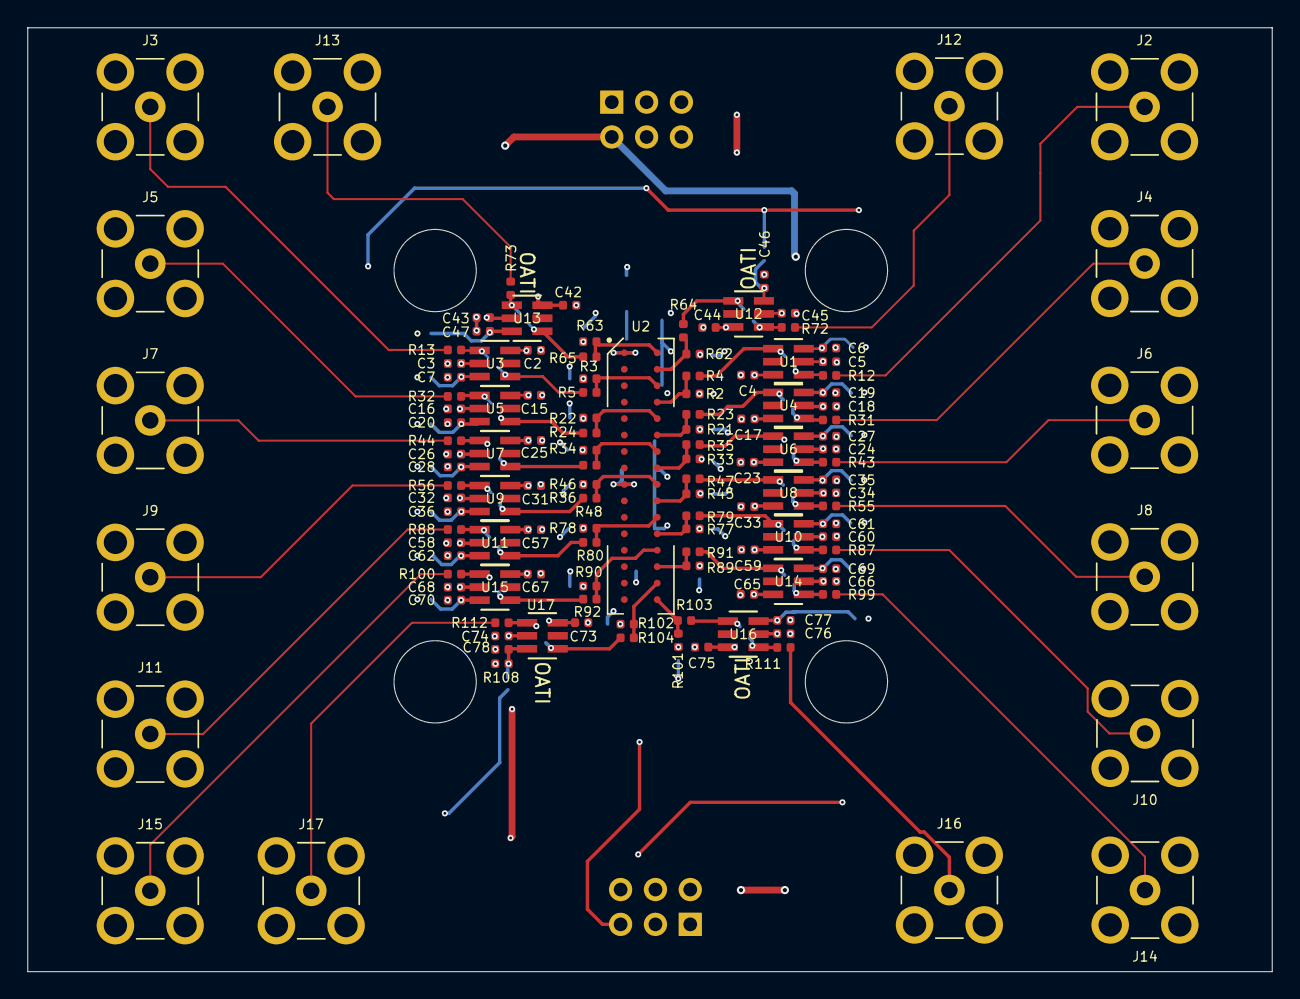
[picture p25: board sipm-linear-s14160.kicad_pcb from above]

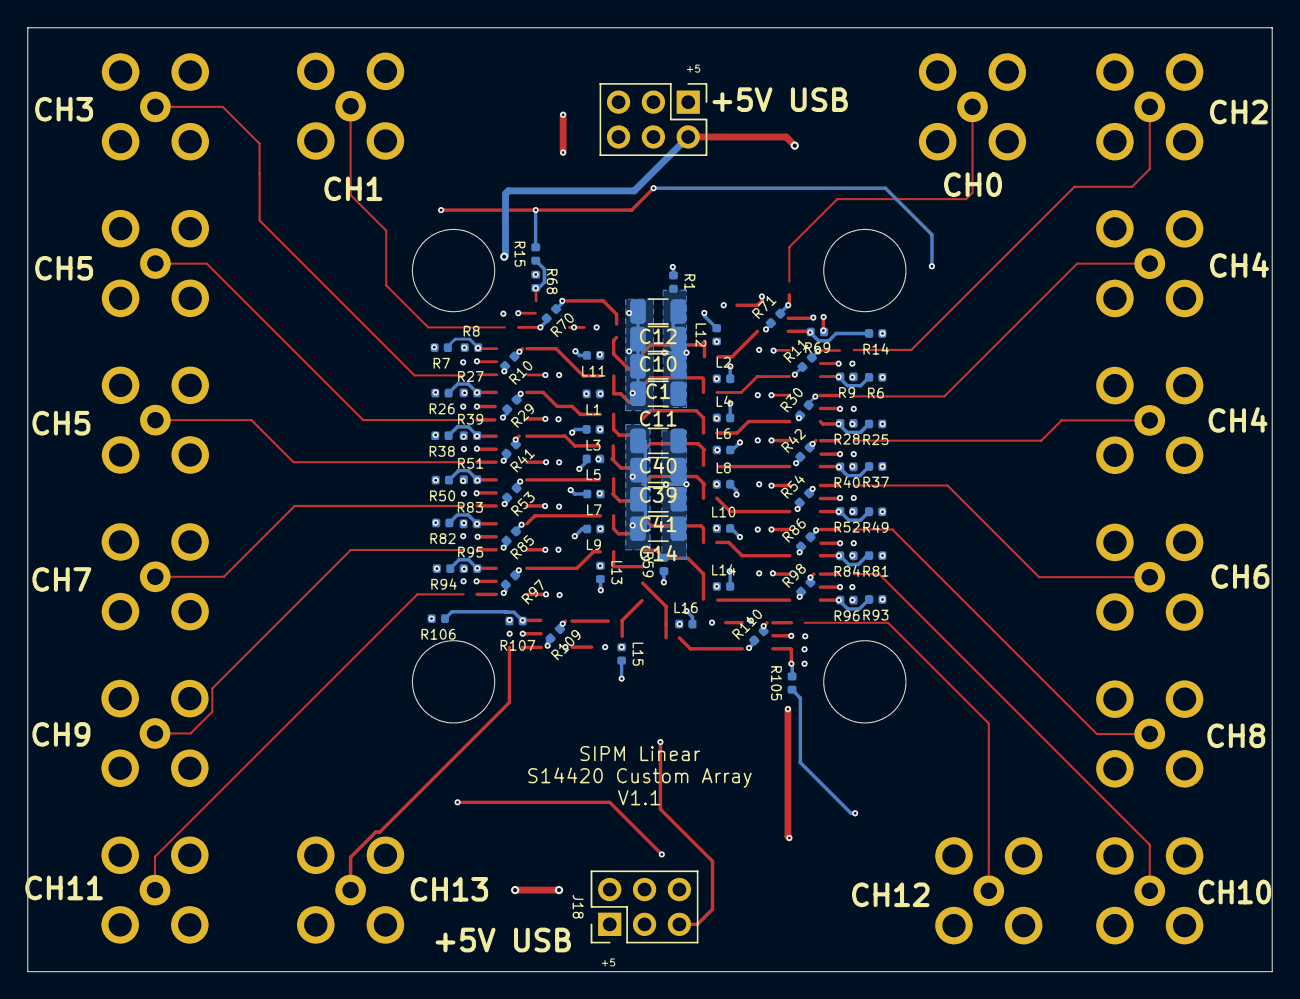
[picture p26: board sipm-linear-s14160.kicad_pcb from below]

Board: 4 copper layers, 90.8 x 68.9 mm, 209 parts (75 on the bottom side), 107 nets.

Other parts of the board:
H1, H2, H3, H4: MountingHole; MountingHole_6mm

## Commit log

2021-08-30 Initial check in of the S15643 linear design files before adapting for the revised S14160 design
    [73415-2061.stp, C_0402_1005Metric.step, C_0603_1608Metric.step, C_0805_2012Metric.step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]
2021-08-30 Update layout for the new footprint
    [SipmPair.kicad_sch, sipm-linear-s15643.kicad_pcb, sipm-linear-s15643.kicad_sch]
2021-10-06 Update layout and fix array footprint
    [SMB standing.step, sipm-linear-s15643.kicad_pcb]
2021-10-06 Update foot print for the revised hamamatsu part
    They only have 2 cathode connections. In addition, add a second power connector, since at least two power supplies are going to be needed.
    [SipmPair.kicad_sch, sipm-linear-s15643.kicad_pcb, sipm-linear-s15643.kicad_sch]
2021-10-07 Add step model for the sipm array
    [AF210729 v2.step, sipm-linear-s15643.kicad_pcb]
2021-10-07 Split power rails across two power supplies
    [SipmPair.kicad_sch, sipm-linear-s15643.kicad_pcb, sipm-linear-s15643.kicad_sch]
2022-01-29 Rename to reflect that we are using the s14160 elements in the array
    [sipm-linear-s14160.kicad_pcb, sipm-linear-s14160.kicad_sch]
2022-01-31 Check in before removing feedback cap
    [SipmPair.kicad_sch, sipm-linear-s14160.kicad_pcb, sipm-linear-s14160.kicad_sch]
2022-02-08 First version that passes schematic parity check
    [sipm-linear-s14160.kicad_pcb]
2022-02-08 Near final version
    Sorted out the line input, flipped the connectors around to the correct board side and cleaned up the silkscreen.
    [sipm-linear-s14160.kicad_pcb]
2022-06-09 Update the PCB with final PZC and offset values
    In testing, the PZC worked well with 6.3/43/90nH on the S14160-1315 which we are assuming is very similar. These values may not be quite right for the array but are hopefully close. The 68/5000 ohm o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
    [SipmPair.kicad_sch, sipm-linear-s14160.kicad_pcb, sipm-linear-s14160.kicad_sch]
2022-07-28 Check in sipm linear manufacturing files
    [sipm-linear-s14160-CuBottom.gbr, sipm-linear-s14160-CuIn1.gbr, sipm-linear-s14160-CuIn2.gbr, sipm-linear-s14160-CuTop.gbr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]
2022-07-28 Change decoupling to 1206
    [SipmPair.kicad_sch, sipm-linear-s14160.kicad_pcb, sipm-linear-s14160.kicad_sch]
2024-09-20 Fix track under drill hole
    Pretty sure JLCPCB quietly fixed this for us on the initial design.
    [SipmPair.kicad_sch, sipm-linear-s14160.kicad_pcb, sipm-linear-s14160.kicad_sch]
2024-09-21 Check in more changes
    Forgot to hit save before last commits.
    [sipm-linear-s14160.kicad_pcb]
2024-09-21 Remove old gerbers
    Don't use these, they aren't the final design.
    [sipm-linear-s14160-CuBottom.gbr, sipm-linear-s14160-CuIn1.gbr, sipm-linear-s14160-CuIn2.gbr, sipm-linear-s14160-CuTop.gbr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]
2024-09-21 Rename project folder
    [73415-2061.stp, AF210729 v2.step, BOM-sipm-linear-s14160.csv, C_0402_1005Metric.step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]
2024-09-21 Add power supplies and bias generator
    Note there are two power supply models, a base one and one that can take power from a second USB device to stay under the 500 mA USB2 limit (works fine on USB3 or USB-C hosts).
    [1217AS-H-3R3N_P3.step, 21-0041B_8_MXM.step, 878980466.stp, ATSAMD21E18A-AFT.stp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]
2024-09-21 Update power supply board for latest kicad
    Silence a bunch of unimportant DRC warnings.
    [bias-control-lt8364-linear.kicad_pcb, bias-control-lt8364-linear.kicad_sch]

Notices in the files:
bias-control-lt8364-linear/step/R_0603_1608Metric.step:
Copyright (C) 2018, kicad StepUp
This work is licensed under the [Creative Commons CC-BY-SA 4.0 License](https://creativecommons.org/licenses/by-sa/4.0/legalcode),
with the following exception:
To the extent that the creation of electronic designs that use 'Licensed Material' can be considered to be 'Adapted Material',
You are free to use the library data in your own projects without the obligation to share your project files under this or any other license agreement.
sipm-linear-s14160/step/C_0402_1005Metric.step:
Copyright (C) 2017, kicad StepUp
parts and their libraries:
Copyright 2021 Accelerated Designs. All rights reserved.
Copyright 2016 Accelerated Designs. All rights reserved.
